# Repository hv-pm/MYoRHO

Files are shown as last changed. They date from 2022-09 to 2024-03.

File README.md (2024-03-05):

# MYoRHO (Myoelectric Robotic Hand Orthosis)
MYoRHO is a Non-invasive Muscle-Machine Interface Open Source Project: Wearable Robotic Hand Orthosis. It has a user-tuned approach to develop a custom robotic hand orthosis for a user by having their metrics (ergonomics and surface myoelectric signals) added in the design cycle.

The project is currently being developed in collaboration with the Laboratory of Neural Engineering and Rehabilitation (<a href="https://sites.google.com/view/leneruel/projetos/proj-b">LENER</a>) at the State University of Londrina.

### Ergonomics
The finger splints is composed of two elements: the (i) ring and the (ii) base.<br>
(i) The ring dimensions are based on the dimensions of the user, this component is responsible for the comfortable fitting of the splint in the finger.
(ii) the base lenght is decided together with the user and it hinders the range of motion, altogether, it defines the curvature of the grasp.<br>
A chamfer connects both elements and allows for the splint to undergo the necessary pressure applied by the grasp without breaking.

The wrist splint is a remixed version of a <a href="https://www.thingiverse.com/thing:706654">public available orthosis</a> for download. This splint size is also modified to fit the user comfortably.

### Surface myoelectric signals (sMES)
The system allows for the developer to train more than the 3 hand poses proposed in this version, although, It should be noted that the current motors disposition only allows 2 hand poses to be reproduced. Thus, system is designed to identify 2 hand poses plus a resting hand state.

An acquisition protocol is estabilished according to the desired number of hand poses, for this prototype, the protocol is designed to acquire the sMES regarding the (i) pulp pinch, (ii) transverse volar grip and a (iii) resting hand pose. By the end of the protocol a sMES dataset is created.<br>
<br>

A sequential forward selection (SFS) is performed with a 10-fold cross-validation method to choose the feature subset used to train the linear discriminant analysis (LDA) classifier of the control system. This subset is chosen based on the best trade-off between the computational power required for processing and accuracy. Twenty datasets are recorded from the user, ten datasets (e.g., even numbered) are reserved to train the LDA classifier, while the other ten datasets (e.g., odd numbered) are used to test the LDA accuracy.

## sMES acquisition platform
<br>
`mSD: microSD module`; `ESP32: DEVKIT V1`; `MyoWare: wearable surface electromyograph`.

This acquisition platform stores real-time recording (datasets) of sMES on a micro SD card. ESP32 was chosen due to its 12-bit analog-to-digital converter (ADC) resolution and compact dimensions. However, given ESP32's problem of non-linearity in ADC readings a <a href="https://github.com/e-tinkers/esp32-adc-calibrate">lookup table calibration</a> is mandatory before recording the datasets. Additionally, a 100 nF ceramic decoupling capacitor is added to attenuate characteristic noises of the ESP32's ADC readings.

The programming interface used for the acquisition platform was the Arduino IDE (v.1.8.1). The code was adapted from the datalogger <a href="https://github.com/greiman/SdFat">example</a> of the SdFat v2.0.6 library, and the chosen baud rate for the serial was 115200 bits/s. Finally, the data were recorded with a sampling rate of 1 kHz.

The sMES signals for each chosen upper limb muscle of the user are analyzed while the user is requested to perform a maximum voluntary contraction (MVC) of a pulp pinch. The muscle with the most significant amplitude is used to record the datasets and activate the system thereafter.

## Transmitter-interpreter system (TIS)
<br>
The TIS module initializes and makes the BLE connection to the RAS module. sMES windows are captured in real-time from MyoWare and converted to millivolts. Next, there is a fourth-order Butterworth (20 to 500 Hz) and notch (60 Hz) digital filtering of the sMES window in which the feature subset is extracted. A linear discriminant analysis (LDA) classifier discriminates the feature subset by comparing the shortest Mahalanobis distance between the feature subset and the center of each class cluster. The closest class to this feature subset (i.e., an unknown sample to the classifier) is chosen and stored in an array of classes. If three classes are added to the array of classes a majority vote (MV) is applied, if not, the class is added to the array, and one more real-time window is filtered, extracted and discriminated. The MV checks which of the three classes stored in the vector occurred with the most frequency and transmits it via BLE to the receiver-actuator system (RAS) module, where its finite state machine will control the orthosis actuators.

## Receiver-actuator system (RAS)
<br>
Auxiliary to the LDA classifier at TIS, a finite-state machine was implemented at RAS to limit the movements that could be performed while the system was in specific states, reducing system failures. It has three main variables: `current state` keeps track of which grip is being performed at the moment; `received class` holds the current class received from TIS; `previously received` saves the value of `received class` before a new transmission overwrites it. As stated earlier, TIS can transmit three different classes: pinch grip (PG), cylindrical grip (CG), and resting hand (RH).

RAS initializes and establishes the BLE connection with TIS. The motors rotate the tendons until the fingers position when shutting down (saved in ESP32's EEPROM) reaches the resting hand (RH) position, and the `current state` becomes RH. This prompted behavior is necessary to ensure that system will always start at the RH pose. Also, if an unusual malfunction in the finite-state machine occurs, causing the motors' position to behave differently from the programmed in the finite-state machine, simply turning off and turning on the device will correct the motors' positions.

When TIS transmits a new class, RAS checks in the variable `current state` which hand pose is being reproduced and decides which pose will be performed based on the analysis of `current state`, `received class` and `previously received`. Any grip (PG or CG) can only be performed if `current state` is RH. Similarly, a grip can only be released if `previously received` is RH and `received class` is its respective grip.

For instance, the motors will only perform PG if `current state` is RH (i.e., the user’s hand is at rest) and the received class is PG. Under these conditions, the motors perform the pinch grip, and `current state` changes to PG. In other words, the user was relaxed and voluntarily performed a pinch grip to activate the orthosis. However, the orthosis will only release the pinch grip when three conditions are met: `current state` is PG, `previously received` is RH, and `received class` is PG. That is, the orthosis is performing a pinch grip, but the muscle is relaxed. Then, the user voluntarily performs another pinch grip to activate the orthosis' release and make the motors rotate to relieve the tension of the tendons.

## Current relase assembly
### TIS module
<br>
`Bat: battery`; `TP4056: USB recharge module for the battery`; `SD: on/off sliding switch`; `Step-up: 3 V to 5 V`; `ESP32: DEVKIT V1`; `D. Cap. 100nf: decoupling capacitor`; `MyoWare: wearable surface electromyograph`.

### RAS module
<br>
`DRV8833: dual h-bridge driver`; `Motors 1 & 2: N20 DC gearbox - 100 RPM rated 6 V`; `ESP32: DEVKIT V1`; `Motors 1 & 2: N20 DC gearbox - 100 RPM rated 6 V`.

## When using MYoRHO in a scientific context, please cite this article:


```
@article{MARTINS2023105014,
  title = {Development of a robotic orthosis for fingers flexion motion by surface myoelectric control: Open source prototype},
  journal = {Biomedical Signal Processing and Control},
  volume = {85},
  pages = {105014},
  year = {2023},
  issn = {1746-8094},
  doi = {https://doi.org/10.1016/j.bspc.2023.105014},
  url = {https://www.sciencedirect.com/science/article/pii/S1746809423004470},
  author = {Hygor Vinícius Pereira Martins and João Antônio Palma Setti and Cayley Guimarães and Daniel Prado Campos},
```

Produto Tecnológico desenvolvido durante projeto de Mestrado "DESENVOLVIMENTO DE UMA ÓRTESE ROBÓTICA PARA O MOVIMENTO DE FLEXÃO DOS QUIRODÁCTILOS POR CONTROLE MIOELÉTRICO: PROTÓTIPO EM CÓDIGO ABERTO" do Programa de Pós-graduação em Engenharia Biomédica da UTFPR - Campus Curitiba, sob orientação do professor Dr. Daniel Prado de Campos. 

## License
<div>
  <div>
    <span>3D files licensed under</span><br>
    
  </div>
  <div>
    <span>Codes licensed under</span><br>
    
  </div>
</div>

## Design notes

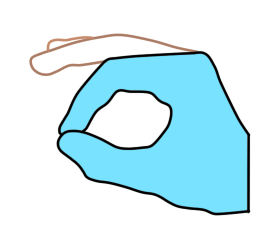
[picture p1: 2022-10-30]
CODES/MYoRHO.ino Generator/main/Pinches/PPm1.png

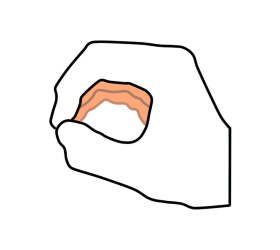
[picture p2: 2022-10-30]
CODES/MYoRHO.ino Generator/main/Pinches/PCm2.png

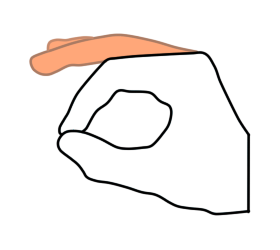
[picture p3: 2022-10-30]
CODES/MYoRHO.ino Generator/main/Pinches/PPm2.png

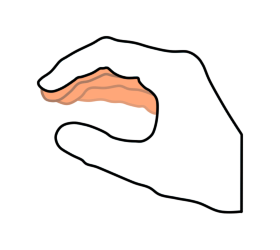
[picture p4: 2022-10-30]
CODES/MYoRHO.ino Generator/main/Pinches/MRm2.png

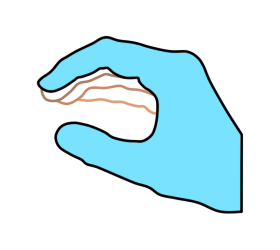
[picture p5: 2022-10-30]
CODES/MYoRHO.ino Generator/main/Pinches/MRm1.png

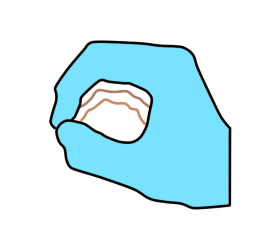
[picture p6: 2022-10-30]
CODES/MYoRHO.ino Generator/main/Pinches/PCm1.png

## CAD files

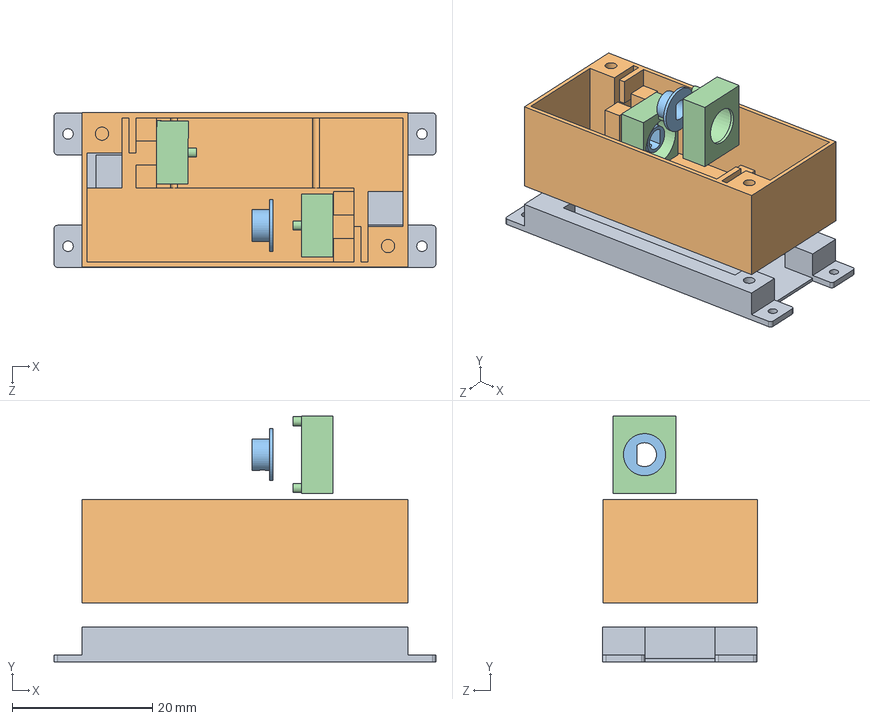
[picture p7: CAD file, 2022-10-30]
3D FILES/Case Motores_Driver/Montagem.SLDASM
54.4 x 35.0 x 22.0 mm
driverboxv2
finalbox
P1-6 x 2
P2-4 x 2

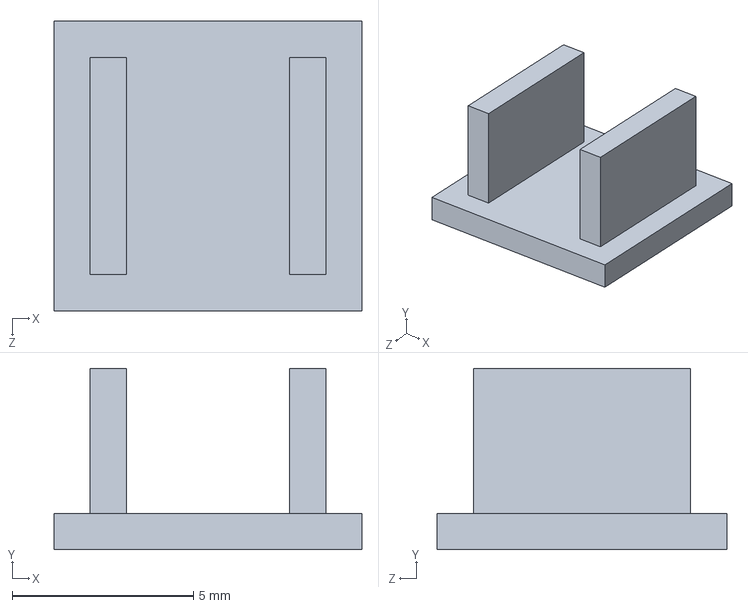
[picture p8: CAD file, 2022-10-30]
3D FILES/Case Alimentação/fixadores.SLDPRT
8.50 x 5.00 x 8.00 mm

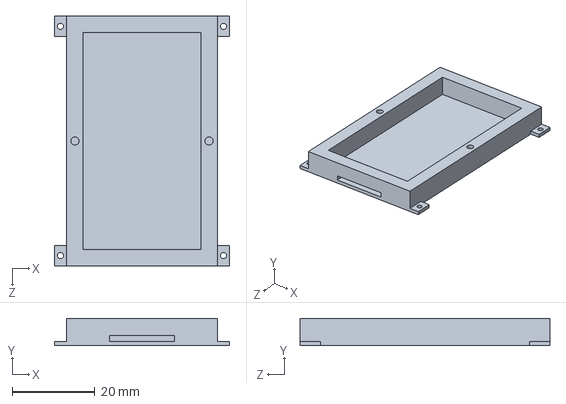
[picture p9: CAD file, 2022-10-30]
3D FILES/Case ESP32/caseMao.SLDPRT
42.4 x 6.60 x 60.4 mm

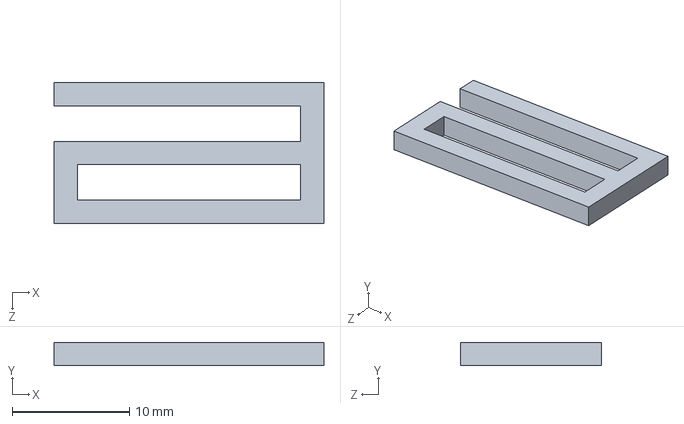
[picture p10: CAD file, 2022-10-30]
3D FILES/Pulseira/encaixe1.SLDPRT
23.0 x 2.00 x 12.0 mm

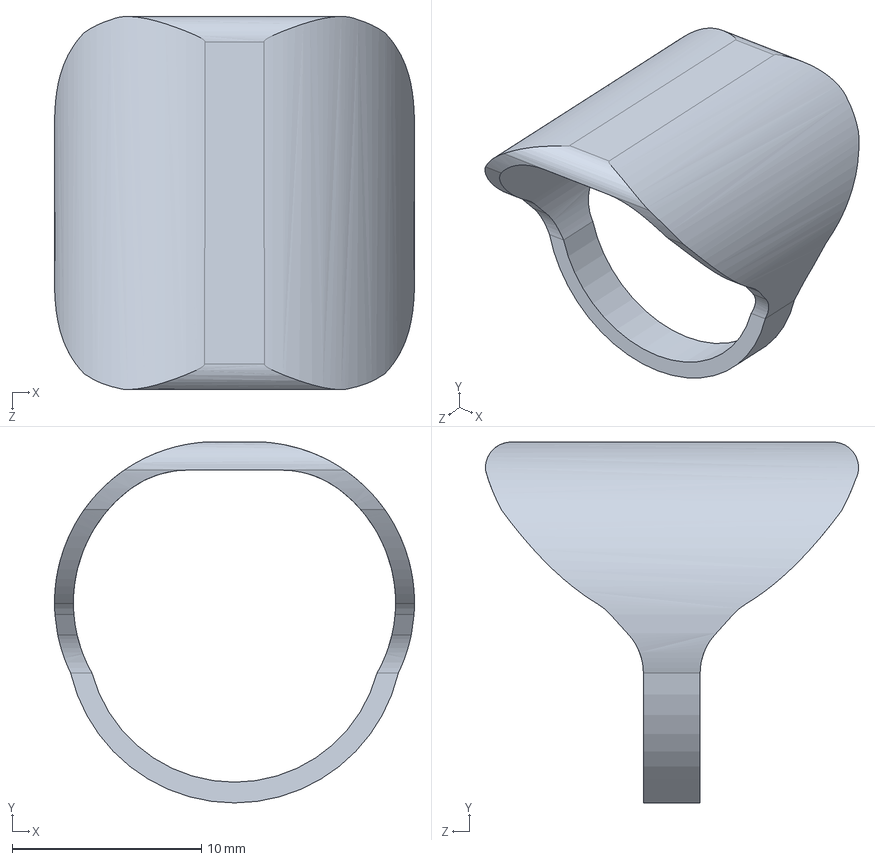
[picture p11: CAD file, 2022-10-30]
3D FILES/Talas Juntas/Minimo_Proximal.SLDPRT
19.0 x 19.0 x 19.7 mm

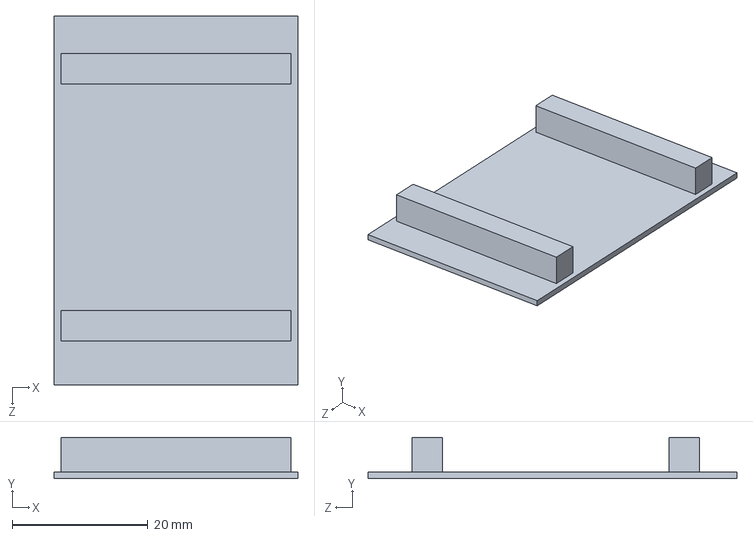
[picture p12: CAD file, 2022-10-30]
3D FILES/Case Alimentação/tampa.SLDPRT
36.0 x 6.10 x 54.4 mm

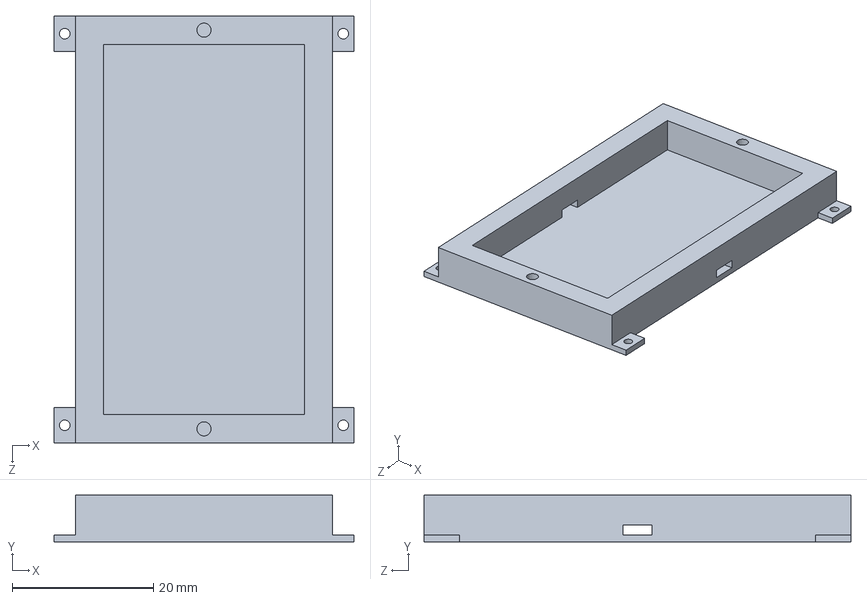
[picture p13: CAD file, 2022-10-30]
3D FILES/Case ESP32/caseSleeve.SLDPRT
42.4 x 6.60 x 60.4 mm

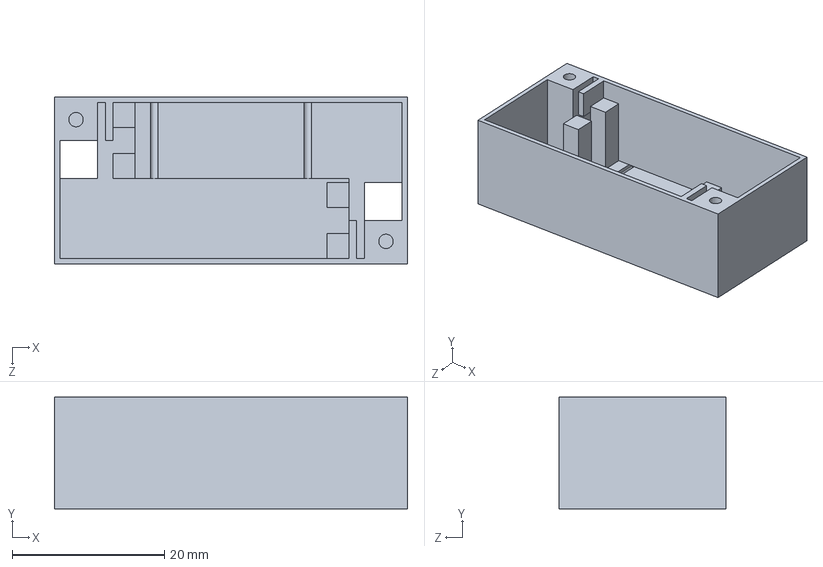
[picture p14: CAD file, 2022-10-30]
3D FILES/Case Motores_Driver/caseMotores.SLDPRT
46.4 x 14.7 x 22.0 mm

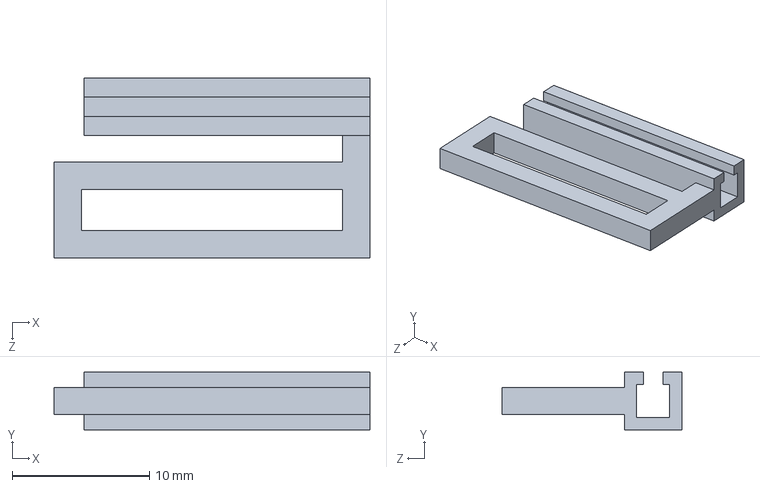
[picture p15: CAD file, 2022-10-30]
3D FILES/Pulseira/encaixe2.SLDPRT
23.0 x 4.20 x 13.1 mm

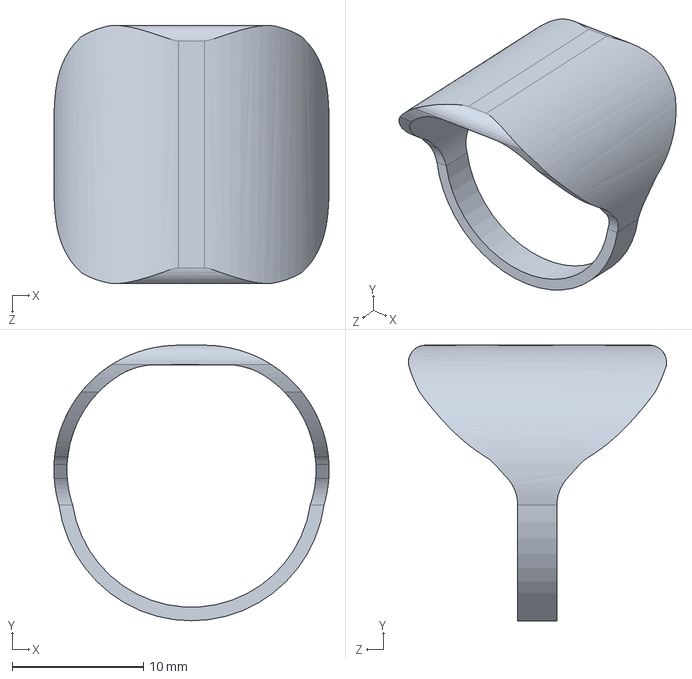
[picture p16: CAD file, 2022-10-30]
3D FILES/Talas Juntas/Medio_Proximal.SLDPRT
21.0 x 21.0 x 19.7 mm

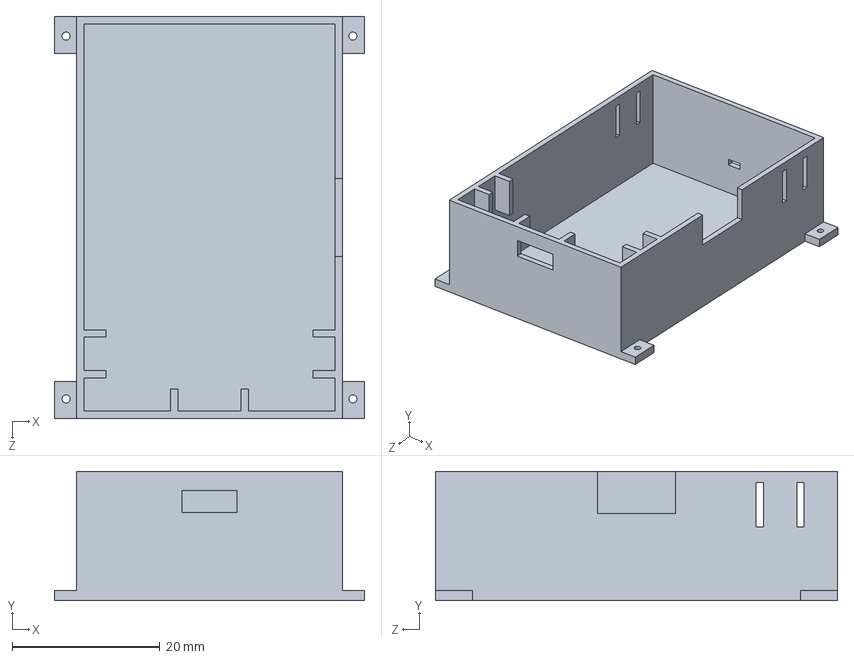
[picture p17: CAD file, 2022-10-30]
3D FILES/Case Alimentação/caseBateria.SLDPRT
42.0 x 17.5 x 54.4 mm

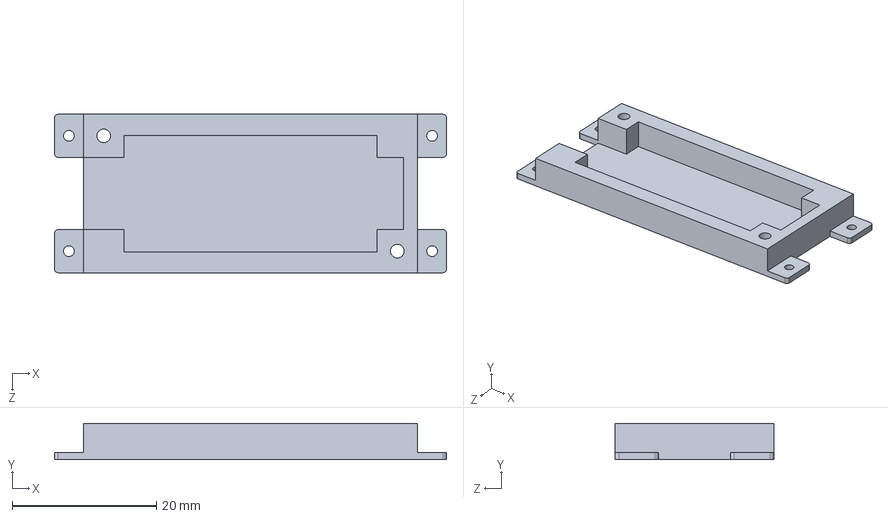
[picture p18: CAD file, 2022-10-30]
3D FILES/Case Motores_Driver/caseDRV8833.SLDPRT
54.4 x 5.00 x 22.0 mm

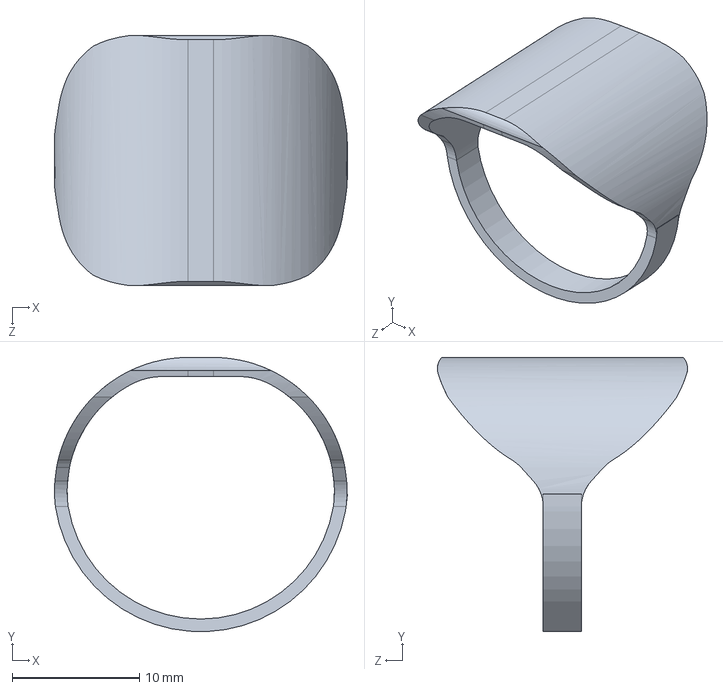
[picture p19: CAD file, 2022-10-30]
3D FILES/Talas Juntas/Polegar_Proximal.SLDPRT
23.0 x 21.5 x 19.7 mm

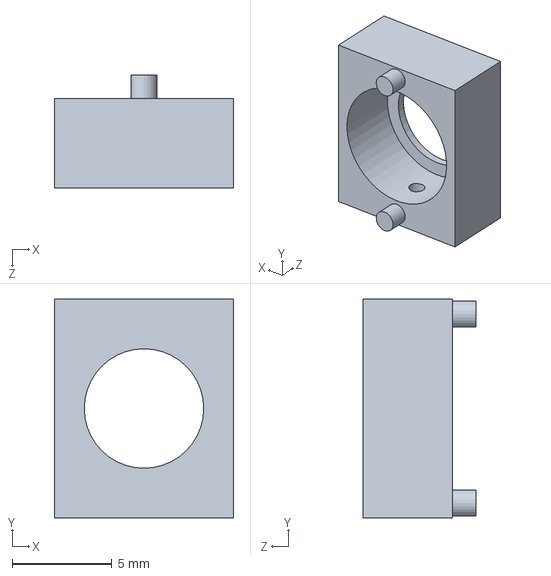
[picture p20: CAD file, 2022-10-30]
3D FILES/Case Motores_Driver/caseSpool.SLDPRT
9.00 x 11.0 x 5.70 mm

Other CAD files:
3D FILES/Talas Juntas/Anelar_Indicador_Proximal.SLDPRT
3D FILES/Case Motores_Driver/spool.SLDPRT
3D FILES/Case Alimentação/caseBateria.STL
3D FILES/Case Alimentação/fixadores.STL
3D FILES/Case Alimentação/tampa.STL
3D FILES/Case ESP32/caseMao.STL
3D FILES/Case ESP32/caseSleeve.STL
3D FILES/Case Motores_Driver/caseDRV8833.STL
3D FILES/Case Motores_Driver/caseMotores.STL
3D FILES/Case Motores_Driver/caseSpool.STL
3D FILES/Case Motores_Driver/spool.STL
3D FILES/Pulseira/encaixe1.STL
3D FILES/Pulseira/encaixe2.STL
3D FILES/Talas Juntas/Anelar_Indicador_Proximal.STL
3D FILES/Talas Juntas/Medio_Proximal.STL
3D FILES/Talas Juntas/Minimo_Proximal.STL
3D FILES/Talas Juntas/Polegar_Proximal.STL

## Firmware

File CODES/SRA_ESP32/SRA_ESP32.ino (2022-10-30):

//-----------------------------------------------------------------------------CABEÇALHO-----------------------------------------------------------------------------
// Autor: Hygor Vinícius Pereira Martins (2022)
//        ESP32_SRA (https://github.com/hv-pm/MYoRHO/blob/main/CODES/SRA_ESP32/SRA_ESP32.ino)
//
// Arduino IDE v1.8.1
//
// Bibliotecas utilizadas: 
//                        BLEDevice (https://github.com/espressif/arduino-esp32/blob/master/libraries/BLE/src/BLEDevice.h)
//                        EEPROM (https://github.com/espressif/arduino-esp32/blob/master/libraries/EEPROM/src/EEPROM.h)
// Adaptado de:
//             BLE client (https://github.com/nkolban/esp32-snippets/blob/master/cpp_utils/tests/BLETests/SampleClient.cpp)

//----------------------------------------------------------------------------BIBLIOTECAS----------------------------------------------------------------------------
#include <EEPROM.h> // Permite alocar os dados de posição dos motores DC na memória EEPROM do ESP32.
#include "BLEDevice.h" // Permite uso dos comandos do bluetooth de baixa energia da plataforma ESP32.

//---------------------------------ENCODERS---------------------------------
volatile const byte Encoder_Pa1 = 22; // Pino de fase A do encoder do Motor 1 (PA1).
volatile const byte Encoder_Pb1 = 21; // Pino de fase B do encoder do Motor 1 (PB1).
volatile const byte Encoder_Pa2 = 27; // Pino de fase A do encoder do Motor 2 (PA2).
volatile const byte Encoder_Pb2 = 14; // Pino de fase B do encoder do Motor 2 (PB2).

//--------------------------------PIN MOTOR--------------------------------
int IN1 = 26; // Pino M1- <-> Bout1 <-> DRV8833 <-> Bin1 do Motor 1.
int IN2 = 25; // Pino M1+ <-> Bout2 <-> DRV8833 <-> Bin2 do Motor 1.
int IN3 = 18; // Pino M2- <-> Aout1 <-> DRV8833 <-> Ain1 do Motor 2.
int IN4 = 19; // Pino M2+ <-> Aout2 <-> DRV8833 <-> Ain2 do Motor 2.

//------------------------------VAR. GLOBAIS-------------------------------
#define ONBOARD_LED  2 // LED embutido no ESP32.
volatile byte Encoder_Pa1_Last; // Estado anterior do Encoder_Pa1, usado para comparação de fase do encoder.
volatile byte Encoder_Pb2_Last; // Estado anterior do Encoder_Pb2, usado para comparação de fase do encoder.
volatile int posicao_enc1; // Armazena o número de voltas dadas no eixo do motor 1, contadas pelo encoder (posição do motor 1).
volatile boolean Direcao; // Compara o sentido de giro, a depender do sentido, incrementa ou decrementa da posição as voltas dadas no eixo do motor 1.
volatile int posicao_enc2; // Armazena o número de voltas dadas no eixo do motor 2, contadas pelo encoder (posição do motor 2).
volatile boolean Direcao2; // Compara o sentido de giro, a depender do sentido, incrementa ou decrementa da posição as voltas dadas no eixo do motor 2.

// Máquina de Estados Finitos.
// Estados possíveis.
// eMR = estado mão em repouso.
// ePP = estado preensão pinça.
// ePC = estado preensão cilíndrica.

// Estado inicial da Máquina de Estados Finitos.
String estado_atual = "eMR"; // Estado atual definida como mão em repouso no início da máquina de estados finitos.
String cl_an = "MR"; // Classe anterior definida como mão em repouso no início da máquina de estados finitos.
bool primeira_trans = true; // Ativa flag para receber a primeira transmissão do STI ao início do SRA.

//-------------------------------ENDEREÇO_BLE-------------------------------
// Endereço do STI.
static BLEUUID serviceUUID("f57b1135-8c51-4e7b-be18-07b9cfa1507a");
// O endereço do dado que iremos receber.
static BLEUUID    charUUID("ad87f04a-5075-4109-8b84-f0b1b8ed173f");

static boolean doConnect = false;
static boolean connected = false;
static boolean doScan = false;
static BLERemoteCharacteristic* pRemoteCharacteristic;
static BLEAdvertisedDevice* myDevice;
std::string cl_rec;

//------------------------------CONFIGURANDO BLE----------------------------
static void notifyCallback(
  BLERemoteCharacteristic* pBLERemoteCharacteristic,
  uint8_t* pData,
  size_t length,
  bool isNotify) {
  Serial.print("Notifica callback para o endereço ");
  Serial.print(pBLERemoteCharacteristic->getUUID().toString().c_str());
  Serial.print(" de tamanho ");
  Serial.println(length);
  Serial.print("dado: ");
  Serial.println((char*)pData);
}

class MyClientCallback : public BLEClientCallbacks {
    void onConnect(BLEClient* pclient) {
      digitalWrite(ONBOARD_LED, HIGH); // Ao conectar com o STI, acende o LED imbutido no ESP32.
    }

    void onDisconnect(BLEClient* pclient) {
      connected = false;
      Serial.println("onDisconnect");
      digitalWrite(ONBOARD_LED, LOW); // Ao desconectar com o STI, apaga o LED imbutido no ESP32.
    }
};

bool connectToServer() {
  Serial.print("Se conectando a ");
  Serial.println(myDevice->getAddress().toString().c_str());

  BLEClient*  pClient  = BLEDevice::createClient();
  Serial.println(" - Criando cliente SRA");

  pClient->setClientCallbacks(new MyClientCallback());

  pClient->connect(myDevice); // Executa a rotina onResult da classe MyAdvertisedDeviceCallbacks, ao fim desta seção.
  Serial.println(" - Conectado a STI");

  BLERemoteService* pRemoteService = pClient->getService(serviceUUID);
  if (pRemoteService == nullptr) {
    Serial.print("Não foi possível encontrar o endereço do STI, UUID: ");
    Serial.println(serviceUUID.toString().c_str());
    pClient->disconnect();
    return false;
  }
  Serial.println(" - STI encontrado");


  pRemoteCharacteristic = pRemoteService->getCharacteristic(charUUID);
  if (pRemoteCharacteristic == nullptr) {
    Serial.print("Não foi possível encontrar o endereço do dado, UUID: ");
    Serial.println(charUUID.toString().c_str());
    pClient->disconnect();
    return false;
  }
  Serial.println(" - Dado encontrado");

  // Testa a conexão para verificar se está recebendo dados, lê o dado do STI e guarda na variável cl_rec.
  if (pRemoteCharacteristic->canRead()) {
    cl_rec = pRemoteCharacteristic->readValue();
    Serial.print("Teste - A primeira classe recebida de STI é: ");
    Serial.println(cl_rec.c_str());
  }

  if (pRemoteCharacteristic->canNotify())
    pRemoteCharacteristic->registerForNotify(notifyCallback);

  connected = true; //
  return true;
}
/**
   Rotina para escanear os servidoers BLE disponíveis e encontrar STI.
*/
class MyAdvertisedDeviceCallbacks: public BLEAdvertisedDeviceCallbacks {
    /**
        Rotina chamada para cada servidor BLE escaneado, verifica se o servidor é o STI.
    */
    void onResult(BLEAdvertisedDevice advertisedDevice) {
      Serial.print("Servidores BLE encontrados: ");
      Serial.println(advertisedDevice.toString().c_str());

      // Verificando qual deles é tem o endereço do STI.
      if (advertisedDevice.haveServiceUUID() && advertisedDevice.isAdvertisingService(serviceUUID)) {
        BLEDevice::getScan()->stop();
        myDevice = new BLEAdvertisedDevice(advertisedDevice);
        doConnect = true;
        doScan = true;
      } // STI encontrado.
    }
};

//---------------------------------------------------------------------------------------------------SETUP---------------------------------------------------------------------------------------------------
void setup() {
  //---------------------------------EEPROM---------------------------------
  EEPROM.begin(4); // Inicia a EEPROM com o tamanho de 4 bytes.
  Serial.begin(115200); // Taxa de Baud.

  //---------------------ENCONTRANDO SERVIDOR BLE (STI)---------------------
  pinMode(ONBOARD_LED, OUTPUT); // Define o pino 2 (LED imbutido) como saída.
  Serial.println("Iniciando SRA como um cliente BLE...");
  BLEDevice::init("");

  BLEScan* pBLEScan = BLEDevice::getScan(); // Escaneia as servidores BLE.
  pBLEScan->setAdvertisedDeviceCallbacks(new MyAdvertisedDeviceCallbacks()); // Define o método de busca pelo STI como o descrito na classe MyAdvertisedDeviceCallbacks, da seção CONFIGURANDO BLE.
  pBLEScan->setInterval(1349); // O intervalo entre cada scan realizado pelo cliente.
  pBLEScan->setWindow(449); // A quantidade de tempo que o scan fica ativo, deve ser menor que o intervalo.
  pBLEScan->setActiveScan(true); // Ativa o escaneamento ativo, utiliza mais energia mas encontra os servidores mais rapidamente.
  pBLEScan->start(5, false); // Inicia o escaneamento por 5 s utilizando as rotinas da seção CONFIGURANDO BLE, durante este tempo o escaneamento irá respeitar o intervalo e o tempo de atividade cada scanner.

  //-------------------------------Motor 1--------------------------------
  pinMode(IN1, OUTPUT); // Define o pino conectado à M1- como saída.
  pinMode(IN2, OUTPUT); // Define o pino conectado à M1+ como saída.
  // Inicializa Motor 1 em LOW (desligado).
  digitalWrite(IN1, LOW); // Inicia M1- no nível lógico baixo.
  digitalWrite(IN2, LOW); // Inicia M1+ no nível lógico baixo.
  //-------------------------------Motor 2--------------------------------
  pinMode(IN3, OUTPUT); // Define o pino conectado à M2- como saída.
  pinMode(IN4, OUTPUT); // Define o pino conectado à M2+ como saída.
  // Inicializa Motor 2 em LOW (desligado).
  digitalWrite(IN3, LOW); // Inicia M2- no nível lógico baixo.
  digitalWrite(IN4, LOW); // Inicia M2+ no nível lógico baixo.

  //---------------------------INICIAR ENCODER----------------------------
  delay(5000); // Aguarda 5 s para iniciar resgate da posição atual dos Motores 1 e 2.
  Serial.println("Inicializando");
  EncoderInit(); // Executa as rotinas de leitura e interpretação das mudanças de níveis lógicos do encoder.

  Serial.print("Posição M1: ");
  Serial.println(posicao_enc1);
  Serial.print("Posição M2: ");
  Serial.println(posicao_enc2);
  Serial.print(" ");
}

//---------------------------------------------------------------------------------------------------IRAM---------------------------------------------------------------------------------------------------
//----------------------------------------------ENC 1----------------------------------------------
void IRAM_ATTR calculapos1() // IRAM_ATTR força as interrupções na memória RAM, garantindo uma maior velocidade na contagem dos pulsos dos encoders e também evitando que haja overflow do código, já que a ISR é capaz apenas de realizar curtas instruções sem parâmetros ou retorno de variáveis.
{
  int volatile Enc1_atual = digitalRead(Encoder_Pa1);
  if ((Encoder_Pa1_Last == LOW) && Enc1_atual == HIGH) // Se o estado anterior do Encoder 1 for baixo e o atual alto: o motor realizou uma rotação.
  {
    int volatile val = digitalRead(Encoder_Pb1);
    if (val == LOW && Direcao) // Verifica qual a direção da rotação.
    {
      Direcao = false; // Sentido anti-horário.
    }
    else if (val == HIGH && !Direcao)
    {
      Direcao = true;  // Sentido horário.
    }
  }
  Encoder_Pa1_Last = Enc1_atual;
  if (!Direcao) {
    posicao_enc1++; // Incrementa encoder se M1 estiver rodando no sentido horário.
  }
  else  {
    posicao_enc1--; // Decrementa encoder se M1 estiver rodando no sentido anti-horário.
  }
}

//----------------------------------------------ENC 2----------------------------------------------
void IRAM_ATTR calculapos2()
{
  int Enc2_atual = digitalRead(Encoder_Pb2);
  if ((Encoder_Pb2_Last == LOW) && Enc2_atual == HIGH)
  {
    int val2 = digitalRead(Encoder_Pa2);
    if (val2 == LOW && Direcao2)
    {
      Direcao2 = false; // Sentido anti-horário.
    }
    else if (val2 == HIGH && !Direcao2)
    {
      Direcao2 = true;  // Sentido horário.
    }
  }
  Encoder_Pb2_Last = Enc2_atual;
  if (!Direcao2) {
    posicao_enc2++; // Incrementa encoder se M2 estiver rodando no sentido horário.
  }
  else  {
    posicao_enc2--; // Decrementa encoder se M2 estiver rodando no sentido anti-horário.
  }
}
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

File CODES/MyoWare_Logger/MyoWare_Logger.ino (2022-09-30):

/*
   Simple data logger.
   Adapted from sdfat library example "dataLogger" by Hygor Vinícius for the LDA_Bundle @ https://github.com/hv-pm/LDA_Bundle
   sampling Ipsilateral Brachioradialis Muscle
*/

//-------------------------------SPECIFICATIONS-------------------------------
/* Board: ESP32 DEV MODULE, default configuration.
 * Library: SdFat by Bill Greiman v2.0.6
 * Arduino IDE v1.8.1
 */

#include <Arduino.h>
#include <driver/dac.h>
#define ADC_PIN 32

#include <SPI.h>
#include "SdFat.h"

// SD chip select pin.  Be sure to disable any other SPI devices such as Enet.
const uint8_t chipSelect = SS;

// Log file base name.  Must be six characters or less.
#define FILE_BASE_NAME "Data"
//------------------------------------------------------------------------------
// File system object.
SdFat sd;

// Log file.
SdFile file;

int i = 0; //milisegundos
int l = 0; //index da label
int cont = 0;
int prevmili = 0;
//==============================================================================
// User functions.  Edit writeHeader() and logData() for your requirements.

const uint8_t ANALOG_COUNT = 1; //número de colunas no header após a primeira, no caso, a quantidade de canais
//------------------------------------------------------------------------------
// Write data header.
void writeHeader() {
  file.print(F("micros")); //primeira coluna
  file.print(F(",label")); //primeira coluna
  for (uint8_t i = 0; i < ANALOG_COUNT; i++) {
    file.print(F(",CHN"));
    file.print(i, DEC);
  }
  file.println();
}
//==============================================================================
// Error messages stored in flash.
#define error(msg) sd.errorHalt(F(msg))
//------------------------------------------------------------------------------
// Lookup Table
const float ADC_LUT[4096] = { 0,
72.4000,80.8000,81.8000,82.8000,84.0000,85.0000,86.0000,87.0000,88.0000,89.2000,90.2000,91.4000,92.6000,93.6000,94.8000,
95.8000,96.8000,97.8000,98.8000,99.8000,100.8000,101.8000,102.8000,103.8000,104.8000,105.8000,107.0000,108.0000,109.0000,110.0000,
111.0000,112.0000,113.0000,114.0000,115.0000,116.0000,117.0000,118.0000,119.0000,120.0000,121.0000,122.0000,123.0000,124.0000,125.0000,
126.0000,127.0000,128.0000,129.0000,130.0000,131.0000,132.0000,133.0000,134.0000,135.0000,136.0000,137.0000,138.0000,139.0000,140.0000,
141.0000,142.0000,143.0000,144.0000,145.2000,146.8000,148.0000,149.8000,151.0000,152.6000,154.0000,155.4000,156.8000,158.0000,159.8000,
161.0000,162.2000,163.8000,164.8000,166.0000,167.6000,168.8000,170.0000,171.2000,172.8000,173.8000,175.0000,176.4000,177.4000,178.4000,
179.2000,180.2000,181.2000,182.2000,183.0000,184.0000,185.0000,186.0000,187.0000,188.0000,189.0000,190.0000,191.0000,192.0000,193.0000,
194.6000,195.8000,197.0000,198.2000,199.8000,200.8000,202.0000,203.4000,204.8000,206.0000,207.0000,208.6000,209.6000,210.6000,211.6000,
212.8000,213.8000,214.8000,215.8000,216.8000,217.8000,218.8000,219.8000,220.8000,221.8000,222.8000,223.8000,225.0000,226.0000,227.2000,
228.6000,229.8000,230.8000,232.0000,233.0000,234.4000,235.6000,236.8000,237.8000,239.0000,240.0000,241.8000,242.8000,244.0000,245.6000,
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

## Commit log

2022-10-30 Rename ESP32_LDA.m to CODES/ESP32_LDA.m
    Reallocated.
2022-10-30 Add files via upload
    Added.
    [Anelar_Indicador_Proximal.SLDPRT, Anelar_Indicador_Proximal.STL, Medio_Proximal.SLDPRT, Medio_Proximal.STL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]
